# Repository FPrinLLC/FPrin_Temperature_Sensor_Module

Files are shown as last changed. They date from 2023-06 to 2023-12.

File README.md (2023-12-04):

# FPrin Temperature Sensor Module Development
Temperature measurement devices are ubiquitous in engineering and other scientific fields because temperature is a parameter that affects nearly all systems and is often essential to measure and control. Through recent work at FPrin involving temperature measurement and analysis we surveyed a series of temperature sensors and found that many common sensors have a surprisingly large rated accuracy specification. For example, perhaps the most used type of temperature measurement device, the thermocouple, typically has a range of ±1-2 °C. For some applications this is an acceptable level of accuracy, but often is insufficient. FPrin aims to develop a cost-effective, easy to build and program, highly accurate, and fully wireless temperature logging solution allowing for easily accessible, high confidence temperature measurement.

For FPrin's previously designed wired temperature sensor module, the design files can be found here:

[Wired Temperature Sensor Module Design](/z_Legacy-Designs/USB_Temperature_Sensor)

## Wireless Temperature Sensing Module
Step 2-2-2-5a

### Features:
- AS6221 Digital Temperature Sensor with rated accuracy of ±0.09 °C
- 3D Printed PLA Enclosure
- Assembly in under 1 hour
- Bluetooth Low Energy (BLE) Supported Data Logging
- High Capacity 2000 mAh Battery
- Companion MATLAB Application for visualization and Logging
- Programmable with Arduino IDE

### Datalogging Interface
To visualize and record data, we have written a MATLAB application that can easily connect with the temperature sensor module, and plot data at a desired frequency.



We've also saved a version of the app as an executable file, this way you won't need a license of MATLAB to use the application.

### Where to get started:
To get started with the temperature sensor module, check out the documentation:
- [User Manual](/FPR12104-00_2_RPT_Wireless_Temperature_Sensor_Module_User_Manual.pdf) : Guide for building, programming, and setting up the module
- [Bill of Materials](/FPR12096-00_1_BOM_Temperature_Sensor_Module.xlsx) : A full list of everything you'll need to build the module
- [MATLAB Application](/MATLAB-Application): A simple desktop app that allows you to connect to a temperature sensor module and log data
- [3D Print Files](/3D-Print-Files): STL and STEP Files for 3D printing the plastic housing
- [Microcontroller Source Code](/TemperatureSensor): Microcontroller source code used with Adafruit nRF52840 Dev Board

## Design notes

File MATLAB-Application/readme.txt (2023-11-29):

TemperatureSensorDatalogger Executable

1. Prerequisites for Deployment 

Verify that MATLAB Runtime(R2023b) is installed.   
If not, you can run the MATLAB Runtime installer.
To find its location, enter
  
    >>mcrinstaller
      
at the MATLAB prompt.
NOTE: You will need administrator rights to run the MATLAB Runtime installer. 

Alternatively, download and install the Windows version of the MATLAB Runtime for R2023b 
from the following link on the MathWorks website:

    https://www.mathworks.com/products/compiler/mcr/index.html
   
For more information about the MATLAB Runtime and the MATLAB Runtime installer, see 
"Distribute Applications" in the MATLAB Compiler documentation  
in the MathWorks Documentation Center.

2. Files to Deploy and Package

Files to Package for Standalone 
================================
-TemperatureSensorDatalogger.exe
-MCRInstaller.exe 
    Note: if end users are unable to download the MATLAB Runtime using the
    instructions in the previous section, include it when building your 
    component by clicking the "Runtime included in package" link in the
    Deployment Tool.
-This readme file 

3. Definitions

For information on deployment terminology, go to
https://www.mathworks.com/help and select MATLAB Compiler >
Getting Started > About Application Deployment >
Deployment Product Terms in the MathWorks Documentation
Center.

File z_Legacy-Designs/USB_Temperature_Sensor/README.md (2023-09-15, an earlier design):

# FPrin Temperature Sensor Module Development
Temperature measurement devices are ubiquitous in engineering and other scientific fields because temperature is a parameter that affects nearly all systems and is often essential to measure and control. Through recent work at FPrin involving temperature measurement and analysis we surveyed a series of temperature sensors and found that many common sensors have a surprisingly large rated accuracy specification. For example, perhaps the most used type of temperature measurement device, the thermocouple, typically has a range of ±1-2 °C. For some applications this is an acceptable level of accuracy, but often is insufficient. FPrin aims to provide a cost-effective, easy to build and program, and most importantly highly accurate temperature sensor module that allows the user to measure ambient temperature with a high degree of confidence.
## Temperature Sensing Module Rev. 1.0
Overview-ScrewBoss

### Features:
- AS6221 Digital Temperature Sensor with rated accuracy of ±0.09 °C
- 3D Printed PLA Enclosure
- Solder-free Assembly in under 1 hour
- Power and Data Transfer with USB Cable
- Programmable with Arduino IDE

### Housing configurations:
Overview-Both

The temperature sensor module has two different style of plastic housing, screw boss (left) and snap fit (right). The screw boss housing is assembled using 4 x thread-forming screws that securely fasten the upper and lower housing together. The snap fit housing uses a plastic flexure to secure the upper and lower housing together and can be removed without any tools.

### Where to get started:
To get started with the temperature sensor module, check out the User Manual and Bill of Materials! The User manual contains a step-by-step guide for building and programming a temperature sensor module in less than 1 hour. The Bill of Materials will tell you everything you need to build a temperature sensor module as well as links to where we bought our materials.

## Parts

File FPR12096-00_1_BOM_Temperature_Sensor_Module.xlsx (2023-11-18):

ASSY NO: |  |  |  | FPR12096
DESCRIPTION: |  |  |  | BLE Temperature Sensor Module
REV: |  |  |  | 1
PROJ # |  |  |  | FPR05
BOM Cost (USD): |  |  |  | $52.01
Item | Qty | UOM | P/N | Title | Vendor | Unit Cost | Total Cost | Link
1 | 0.167 | pack of 6 | B07LFD4LT6 | Solderless Breadboard | Amazon | $8.49 | $1.42 | https://www.amazon.com/gp/product/B07LFD4LT6/ref=ppx_yo_dt_b_asin_title_o02_s00?ie=UTF8&psc=1
2 | 1 | each | 4062 nRF52840 Feather | nRF52840 Feather | Adafruit | $24.95 | $24.95 | https://www.adafruit.com/product/4062
3 | 1 | each | 2011 3.7V Lipo Battery | 2000 mAh 3.7V Lipo Battery | Adafruit | $12.50 | $12.50 | https://www.adafruit.com/product/2011
4 | 1 | each | MIKROE-5466 | MikroE Thermoclick 28 | Mikroelektronika | $11.00 | $11.00 | https://www.mikroe.com/thermo-28-click
5 | 1 | each | FPR12097 | Bottom Housing | N/A | $0.00 | $0.00 | N/A
6 | 1 | each | FPR12098 | Upper Housing | N/A | $0.00 | $0.00 | N/A
7 | 0.08 | pack of 50 | 95495K18 | Rubber Feet | McMaster-Carr | $4.13 | $0.33 | https://www.mcmaster.com/95495k18/
8 | 2 | each | 5862K141 | Neodymium Magnets | McMaster-Carr | $0.77 | $1.54 | https://www.mcmaster.com/5862K141/
9 | 0.16 | pack of 25 | 99461A916 | M2 Threadforming Screws | McMaster-Carr | $8.62 | $1.38 | https://www.mcmaster.com/99461A916/

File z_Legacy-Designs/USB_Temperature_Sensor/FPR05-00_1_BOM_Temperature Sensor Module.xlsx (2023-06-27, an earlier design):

ASSY NO: |  |  | FPR12008
DESCRIPTION: |  |  | DIY Temperature Sensor Module
REV: |  |  | 1
PROJ # |  |  | FPR05
BOM Cost (USD): |  |  | $60.83
Item | Qty | P/N | Title | Vendor | Unit Cost | Link
1 | 1 | B07LFD4LT6 | Solderless Breadboard | Amazon | $7.59 | https://www.amazon.com/gp/product/B07LFD4LT6/ref=ppx_yo_dt_b_asin_title_o02_s00?ie=UTF8&psc=1
2 | 1 | ABX00034 | Arduino Nano 33 BLE | Amazon | $26.40 | https://www.amazon.com/gp/product/B07WXKWNQF/ref=ppx_yo_dt_b_asin_title_o02_s00?ie=UTF8&psc=1
3 | 1 | MIKROE-5466 | MikroE Thermoclick 28 | Mikroelektronika | $11.00 | https://www.mikroe.com/thermo-28-click
4 | 1 | FPR12089 | Bottom Housing | N/A | $0.00 | N/A
5 | 1 | FPR12090 | Upper Housing | N/A | $0.00 | N/A
6 | 1 | 95495K18 | Rubber Feet | McMaster-Carr | $4.13 | https://www.mcmaster.com/95495k18/
7 | 2 | 5862K141 | Neodymium Magnets | McMaster-Carr | $0.77 | https://www.mcmaster.com/5862K141/
8 | 2 | 2.00KXBK-ND | 2k Through-hole Resistor | Digikey | $0.10 | https://www.digikey.com/en/products/detail/yageo/MFR-25FBF52-2K/13070
9 | 1 | 497-16176-2-ND | 3.3V Linear Voltage Regulator | Digikey | $0.54 | https://www.digikey.com/en/products/detail/stmicroelectronics/L78L33ACZTR/1038305
10 | 1 | 399-9882-2-ND | 0.33 μF Ceramic Capacitor | Digikey | $0.49 | https://www.digikey.com/en/products/detail/kemet/C322C334M5U5TA7301/3726083
11 | 1 | 399-9859-2-ND | 0.1 μF Ceramic Capacitor | Digikey | $0.32 | https://www.digikey.com/en/products/detail/kemet/C315C104M5U5TA7303/3726116
12 | 1 | 99461A916 | M2 Threadforming Screws | McMaster-Carr | $8.62 | https://www.mcmaster.com/99461A916/

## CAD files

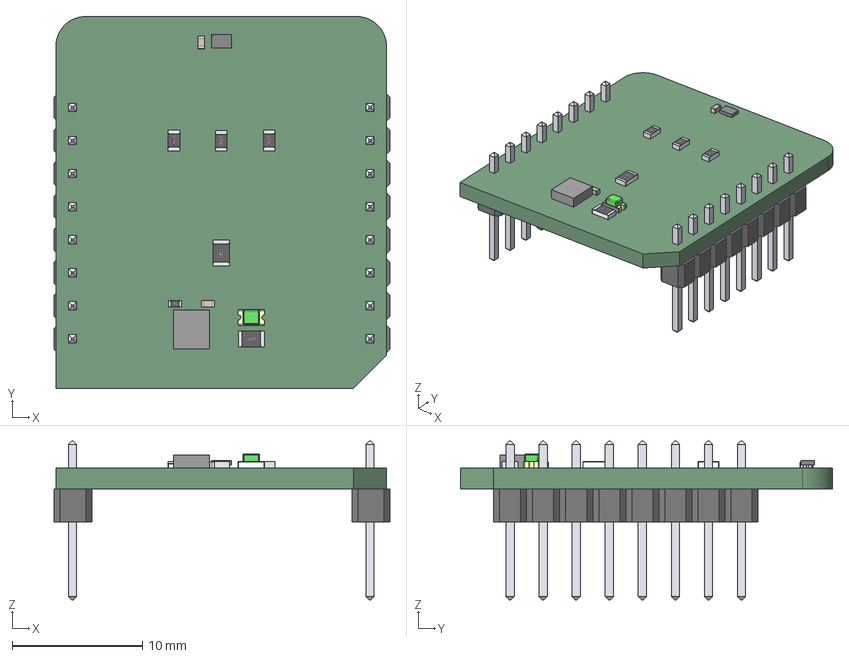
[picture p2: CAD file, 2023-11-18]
CAD/FPR12096/Thermo_28_click_v101.step
25.8 x 28.6 x 12.2 mm
Board
User_Library-R_0402
User_Library-R_0805 x 2
AS6221-AWLT-S_AMS
User_Library-R_0603 x 3
User_Library-SMD_CAPACITOR0402 x 2
User_Library-PinHeaderX5-1_PinHeaderX5_Body_1 x 4
User_Library-PinHeaderX5-1_PinHeaderX5_Pins_1 x 4
led_0805_green
Extruded

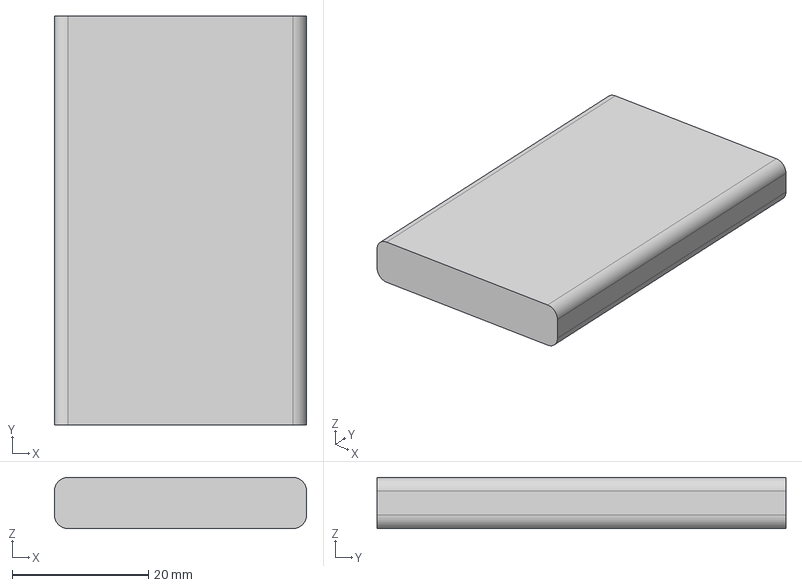
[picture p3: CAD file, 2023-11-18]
CAD/FPR12096/2011 2000mAh Battery.step
37.0 x 60.0 x 7.50 mm

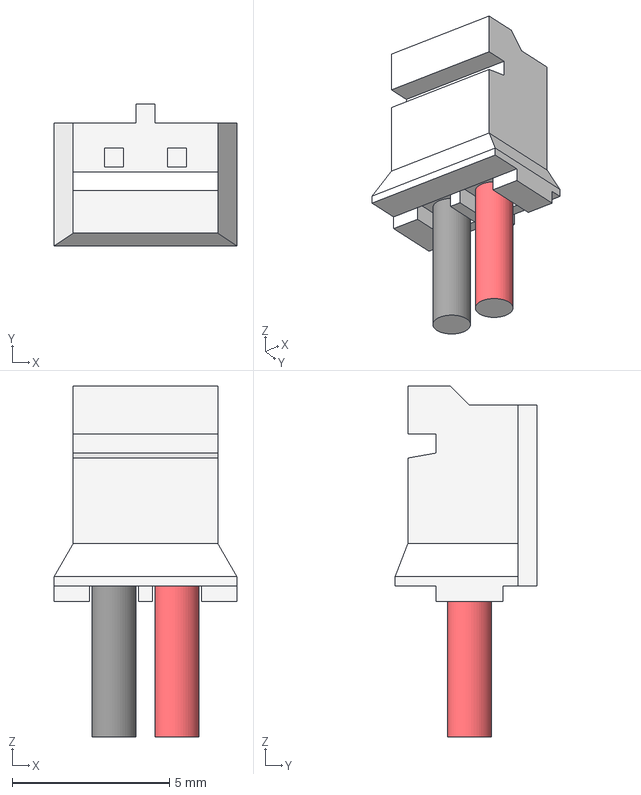
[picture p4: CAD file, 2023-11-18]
CAD/FPR12096/PHR-2-for-Battery-Adafruit.stp
5.80 x 4.50 x 11.2 mm

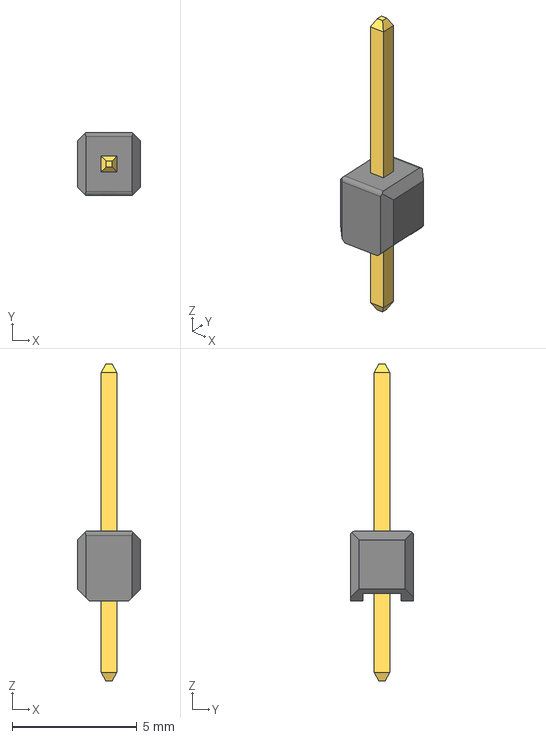
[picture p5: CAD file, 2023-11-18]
CAD/FPR12096/Pin Header 1x1 TH Pitch 2.54mm.stp
2.54 x 2.54 x 12.7 mm

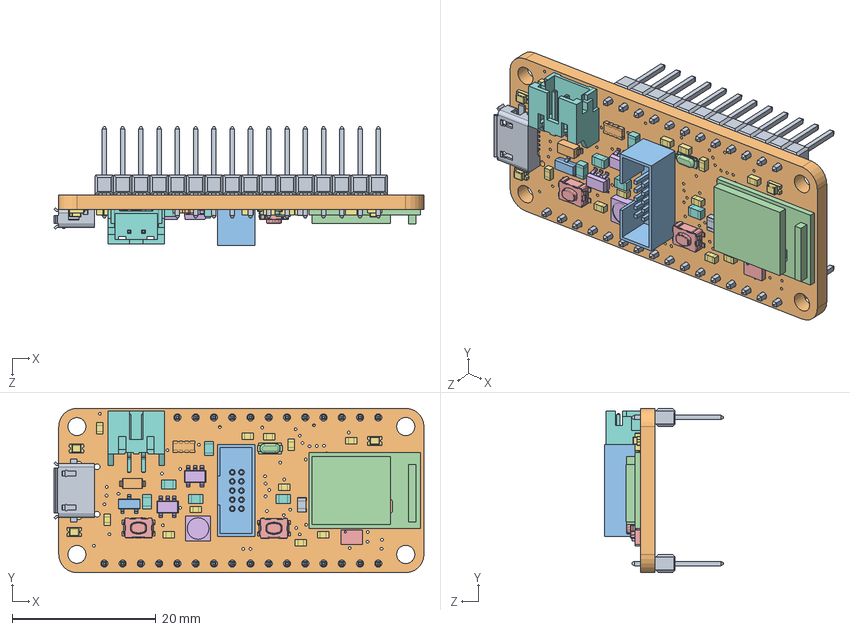
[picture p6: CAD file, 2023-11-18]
CAD/FPR12096/nRF52840 Feather.SLDASM
51.5 x 22.9 x 16.5 mm
Pin Header 1x1 TH Pitch 2.54mm^nRF52840 Feather x 28
Board^PCB Component_4062-nRF52830-Feather_nRF52840 Feather
2x5 0.05_^PCB Component_4062-nRF52830-Feather_nRF52840 Feather
32.768^PCB Component_4062-nRF52830-Feather_nRF52840 Feather
KMR2^PCB Component_4062-nRF52830-Feather_nRF52840 Feather x 2
AP2112(3.3V)^PCB Component_4062-nRF52830-Feather_nRF52840 Feather x 2
BLUE^PCB Component_4062-nRF52830-Feather_nRF52840 Feather x 3
JSTPH^PCB Component_4062-nRF52830-Feather_nRF52840 Feather
4u20329^PCB Component_4062-nRF52830-Feather_nRF52840 Feather
MBR120^PCB Component_4062-nRF52830-Feather_nRF52840 Feather
DMG2305^PCB Component_4062-nRF52830-Feather_nRF52840 Feather
MDBT50^PCB Component_4062-nRF52830-Feather_nRF52840 Feather
GD25Q16^PCB Component_4062-nRF52830-Feather_nRF52840 Feather
WS2812B3535^PCB Component_4062-nRF52830-Feather_nRF52840 Feather
0.1uF^PCB Component_4062-nRF52830-Feather_nRF52840 Feather x 11
10uF^PCB Component_4062-nRF52830-Feather_nRF52840 Feather x 5
DNP^PCB Component_4062-nRF52830-Feather_nRF52840 Feather
100K^PCB Component_4062-nRF52830-Feather_nRF52840 Feather

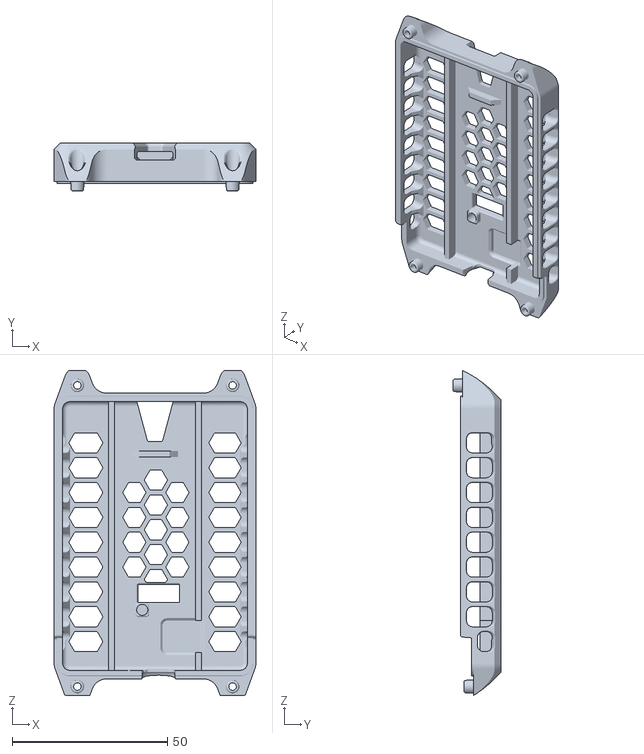
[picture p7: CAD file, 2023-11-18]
3D-Print-Files/FPR12098.STL
65.0 x 15.4 x 104.7

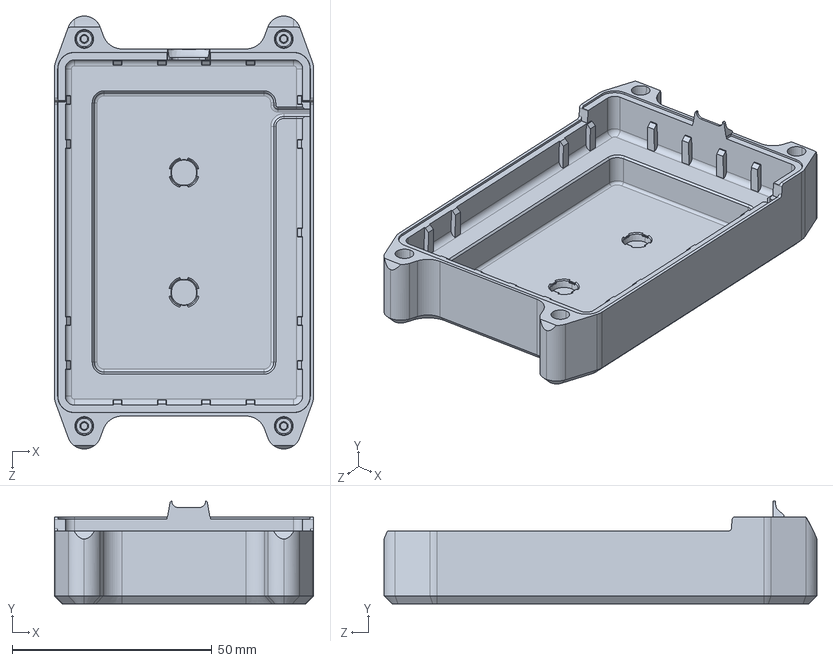
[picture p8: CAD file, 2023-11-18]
3D-Print-Files/FPR12097.STEP
65.0 x 25.8 x 108.5 mm

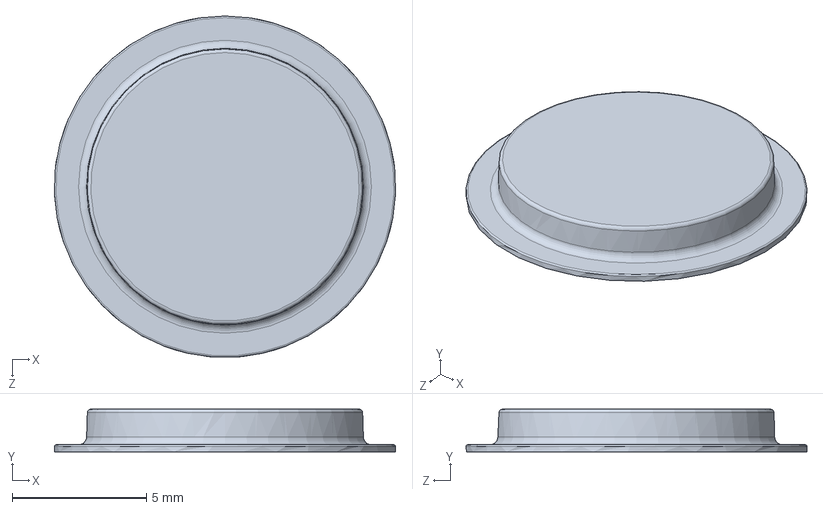
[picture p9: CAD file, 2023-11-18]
CAD/FPR12096/95495K18.SLDPRT
12.7 x 1.59 x 12.7 mm

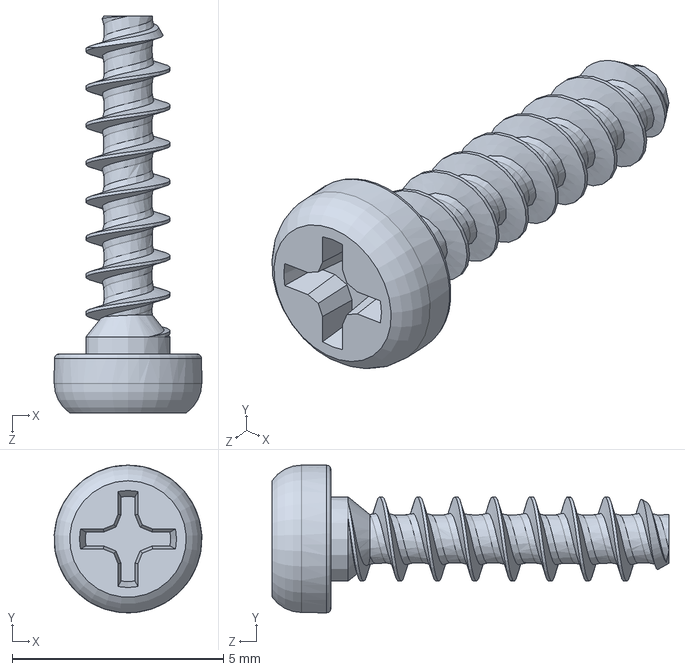
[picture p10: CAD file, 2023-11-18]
CAD/FPR12096/99461A916.SLDPRT
3.49 x 3.50 x 9.40 mm

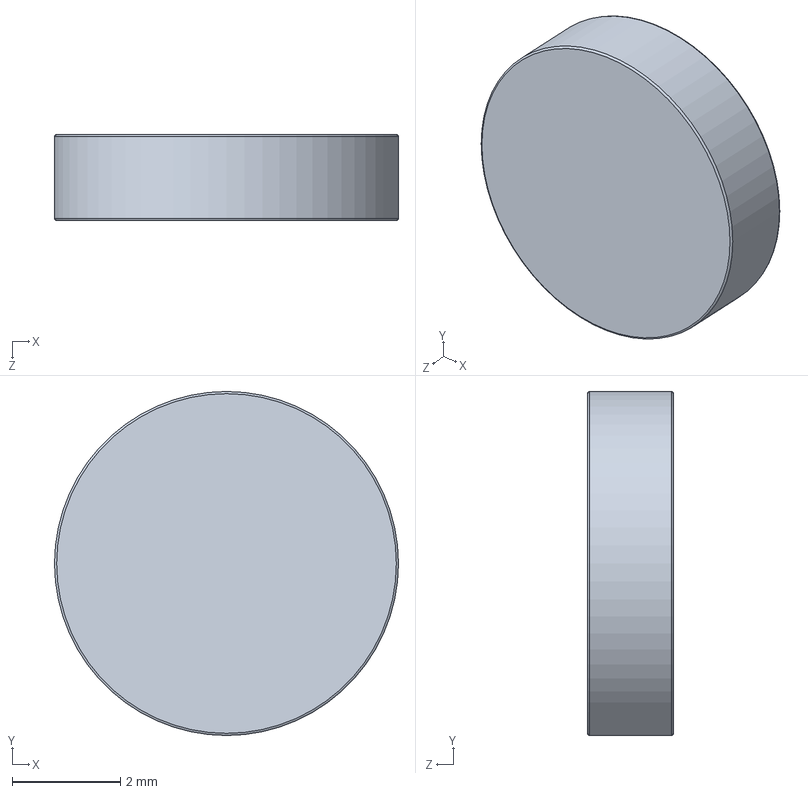
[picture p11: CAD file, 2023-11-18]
CAD/FPR12096/5862K141.SLDPRT
6.35 x 6.35 x 1.59 mm

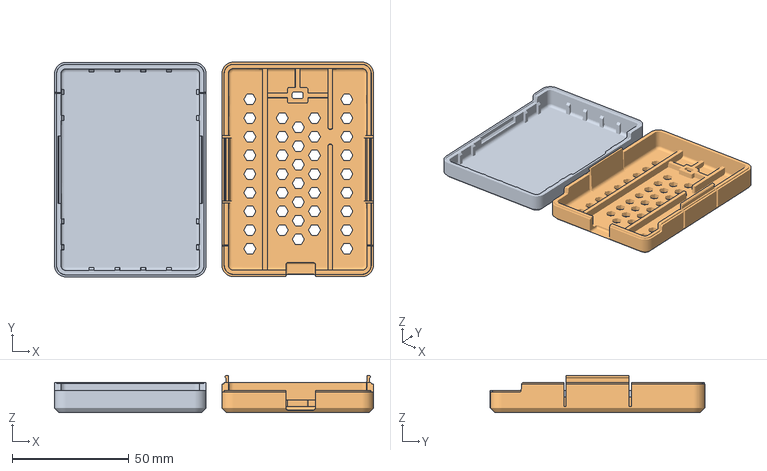
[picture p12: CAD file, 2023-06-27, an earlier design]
z_Legacy-Designs/USB_Temperature_Sensor/3D Print Files/Housing-SnapFit.3mf
136.8 x 92.1 x 16.1 mm
FPR12089-02.STL
FPR12090-02.STL

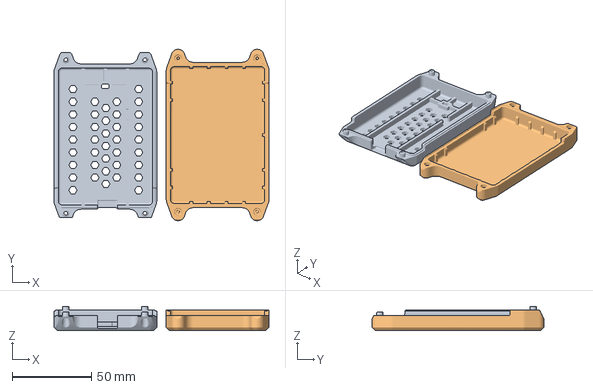
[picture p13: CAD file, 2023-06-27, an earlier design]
z_Legacy-Designs/USB_Temperature_Sensor/3D Print Files/Housing-ScrewBoss.3mf
136.0 x 108.5 x 15.4 mm
FPR12090-02-Screw.STL
FPR12089-02-Screw.STL

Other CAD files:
CAD/FPR12096/FPR12098.SLDPRT
3D-Print-Files/FPR12097.STL

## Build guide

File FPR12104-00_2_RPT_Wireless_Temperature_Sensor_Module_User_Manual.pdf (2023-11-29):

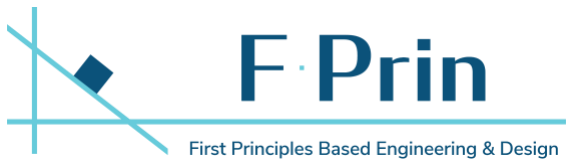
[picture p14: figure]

# BLE Temperature Sensor

# Module User Manual

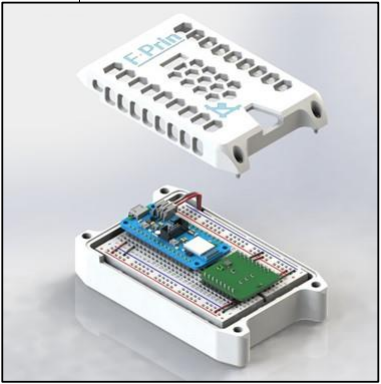
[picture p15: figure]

Document No. | FPR12095
Type | RPT
Revision | 01
State | In-Work
Authors | L Parrish
Project | FP05

BLE Temperature Sensor Module User Manual
Document No. FPR12104 | CONFIDENTIAL
Version: 00.1 | Page 2 of 22

## Contents

1 Introduction | 3
2 Assembly | 3
2.1 | Solderless Breadboard and Circuit | 3
2.1.1 | Materials and Tools | 3
2.1.2 | Solderless Breadboard Assembly Instructions | 5
2.2 | Module Housing | 8
2.2.1 | Materials and Tools | 8
2.2.2 | Module Housing Assembly Instructions | 10
3 Firmware Installation | 13
3.1 | Arduino IDE and nRF Board Manager Installation | 13
3.2 | Firmware Upload | 15
4 Datalogging Setup | 16
4.1 | Connecting to a Temperature Sensing Module | 16
4.2 | Plotting and Sample Frequency Tools | 17
4.3 | Datalogging Tools | 17
5 Revision History | 18
6 Appendix | 19
6.1 | Bill of Materials | 19
6.2 | Circuit Diagram | 20
6.3 | Plastic Part 3D Print Settings | 20

## 1 Introduction

Temperature measurement devices are ubiquitous in engineering and other scientific fields because temperature is a parameter that affects nearly all systems and is often essential to measure and control. Through recent work at FPrin involving temperature measurement and analysis we surveyed a series of temperature sensors and found that many common sensors have a surprisingly wide rated accuracy specification. For example, perhaps the most used type of temperature measurement device, the thermocouple, typically has a range of ±1-2 °C. For some applications this is an acceptable level of accuracy, but often is insufficient. FPrin aims to provide a cost-effective, easy to build and program, and most importantly highly accurate temperature sensor module that allows the user to measure ambient temperature with a high degree of confidence.

A primary development consideration was the accuracy of the temperature sensor used in the module. To achieve this, we incorporated the AS6221 digital temperature sensor from AMS. The integrated circuit features I²C communication for data transmission, low power consumption, and most importantly an excellent temperature accuracy rating of ±0.09 °C. Additionally, all components used to build the module can be easily sourced and assembled with minimal soldering and hand tools. Finally, a housing for the module can be easily fabricated using FDM 3D printing with PLA. The latest design features wireless data transfer to a host PC via Bluetooth Low Energy (BLE) communication and an easy-to-use interface for data visualization and logging. The CAD, Code, and documentation for the project are hosted on FPrin’s GitHub Repository Here:

https://github.com/FPrinLLC/FPrin_Temperature_Sensor_Module.git

## 2 Assembly

### 2.1 Solderless Breadboard and Circuit

### 2.1.1 Materials and Tools

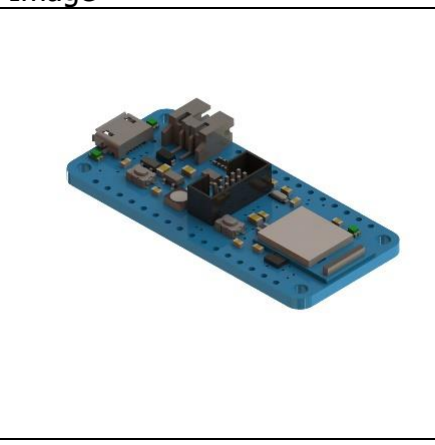
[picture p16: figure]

Description | Quantity | Image
nRF52840 Feather Development Board | 1

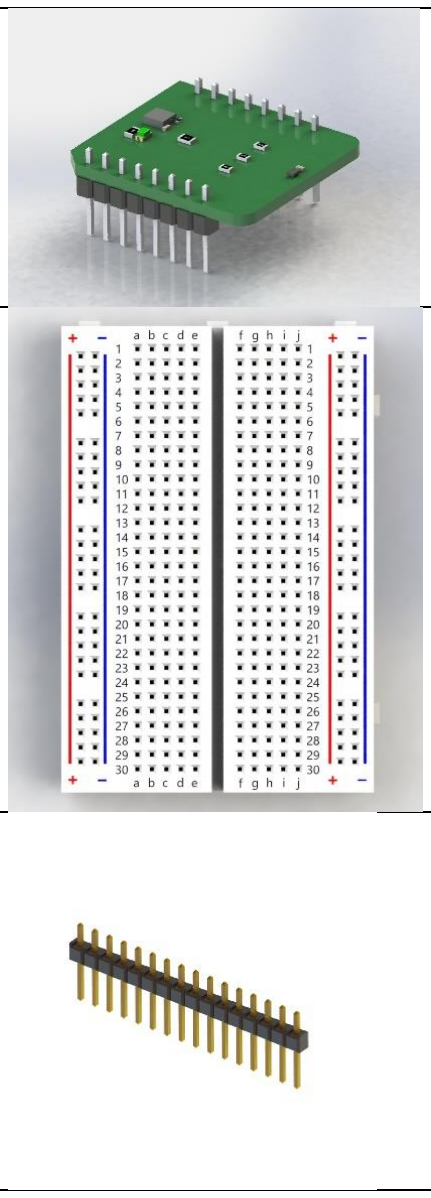
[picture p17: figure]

MikroE Thermo 28 Click PCBA | 1
Solderless Breadboard | 1
0.1” Pin Header Standoffs | 2 x 16
Breadboard Jumper Wires | ~6 inches

The following tools are required to assemble the solderless breadboard and circuit:

- Flush cutters
- Wire Strippers
- Soldering Iron
- Solder

### 2.1.2 Solderless Breadboard Assembly Instructions

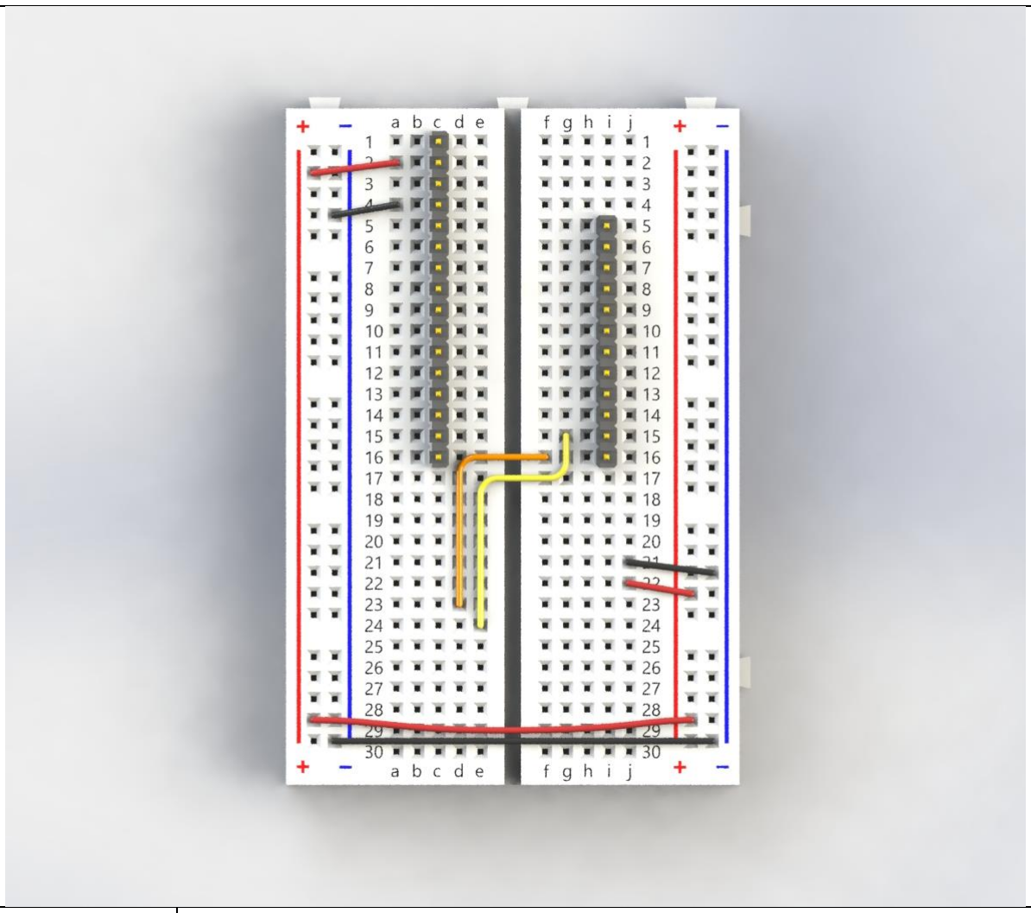
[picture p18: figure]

Step 1: | Install the pin headers into the solderless breadboard with the first row starting at position C1. Then cut the second pin header to remove 4 positions from the end, then install into position I5. Note that both rows should end at row 16.
Step 2: | Cut prototyping wire to length and insert into the breadboard as shown in the image above. Note that the wires should be pressed down flush to the top surface of the breadboard.

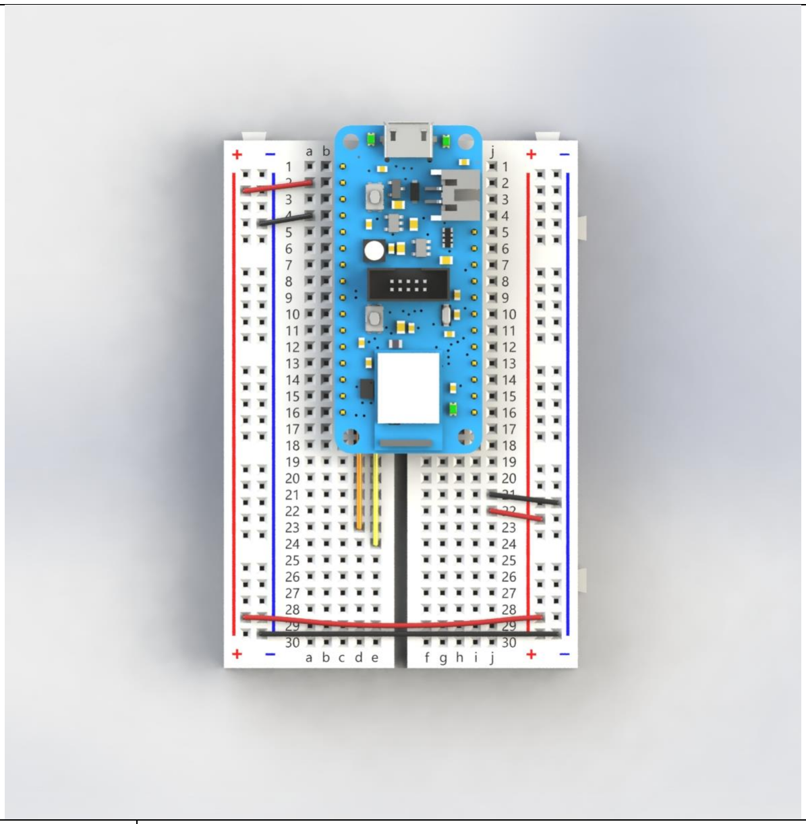
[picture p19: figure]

Step 3: | Place the nRF52840 Feather Dev. Board onto the pin headers as shown. Note that the upper left pin next to the USB connector is in breadboard position c1.
Step 4: | Solder the pin headers in place to secure the electrical connection using a soldering iron and solder.

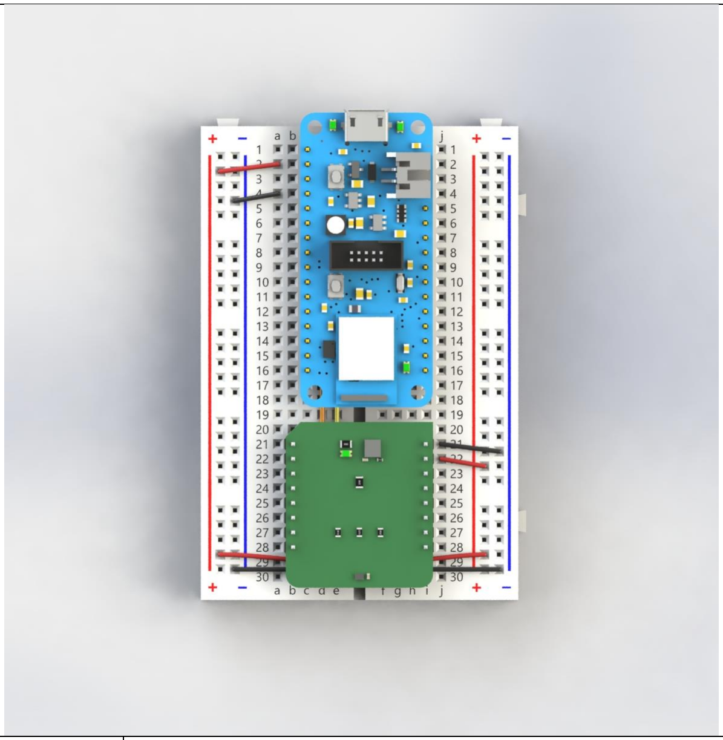
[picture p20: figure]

Step 5: | Press the MikroE Thermo 28 Click PCBA into the breadboard as shown. Note the pin labeled 3V3 should be in breadboard position I22.

### 2.2 Module Housing

### 2.2.1 Materials and Tools

The following parts are required to assemble the module housing:
Description | Quantity | Image
Solderless Breadboard Assembly | 1

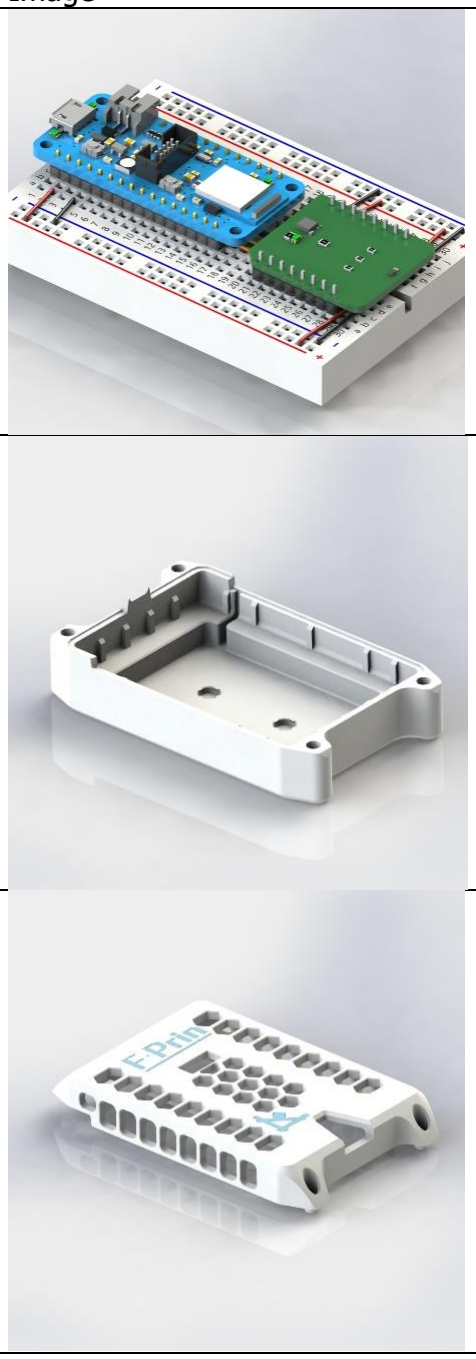
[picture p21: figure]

Housing Lower Half | 1
Housing Upper Half | 1

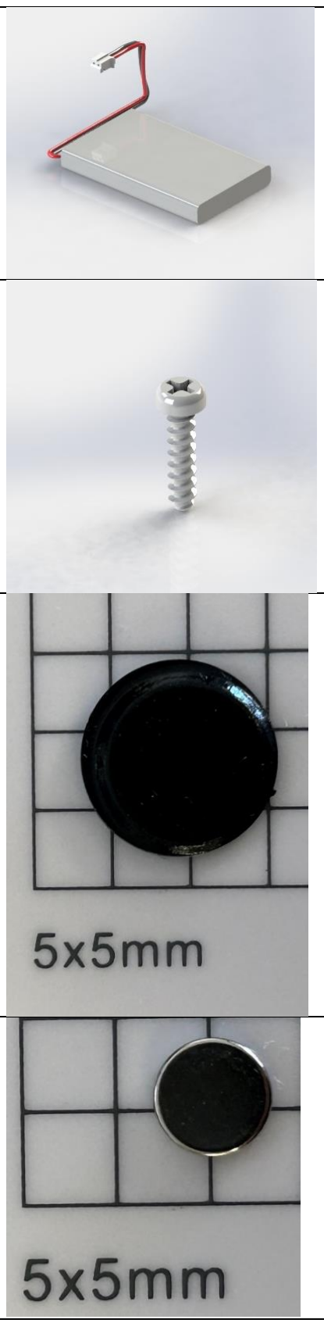
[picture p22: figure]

2000 mAh Li-Poly Battery | 1
Thread-forming Screws for Plastic | 4
Rubber Feet | 4
1/16” Thick, ¼” Neodymium Magnets* | 2

Assembly Tools:

- Size J0 Phillips Screw Driver

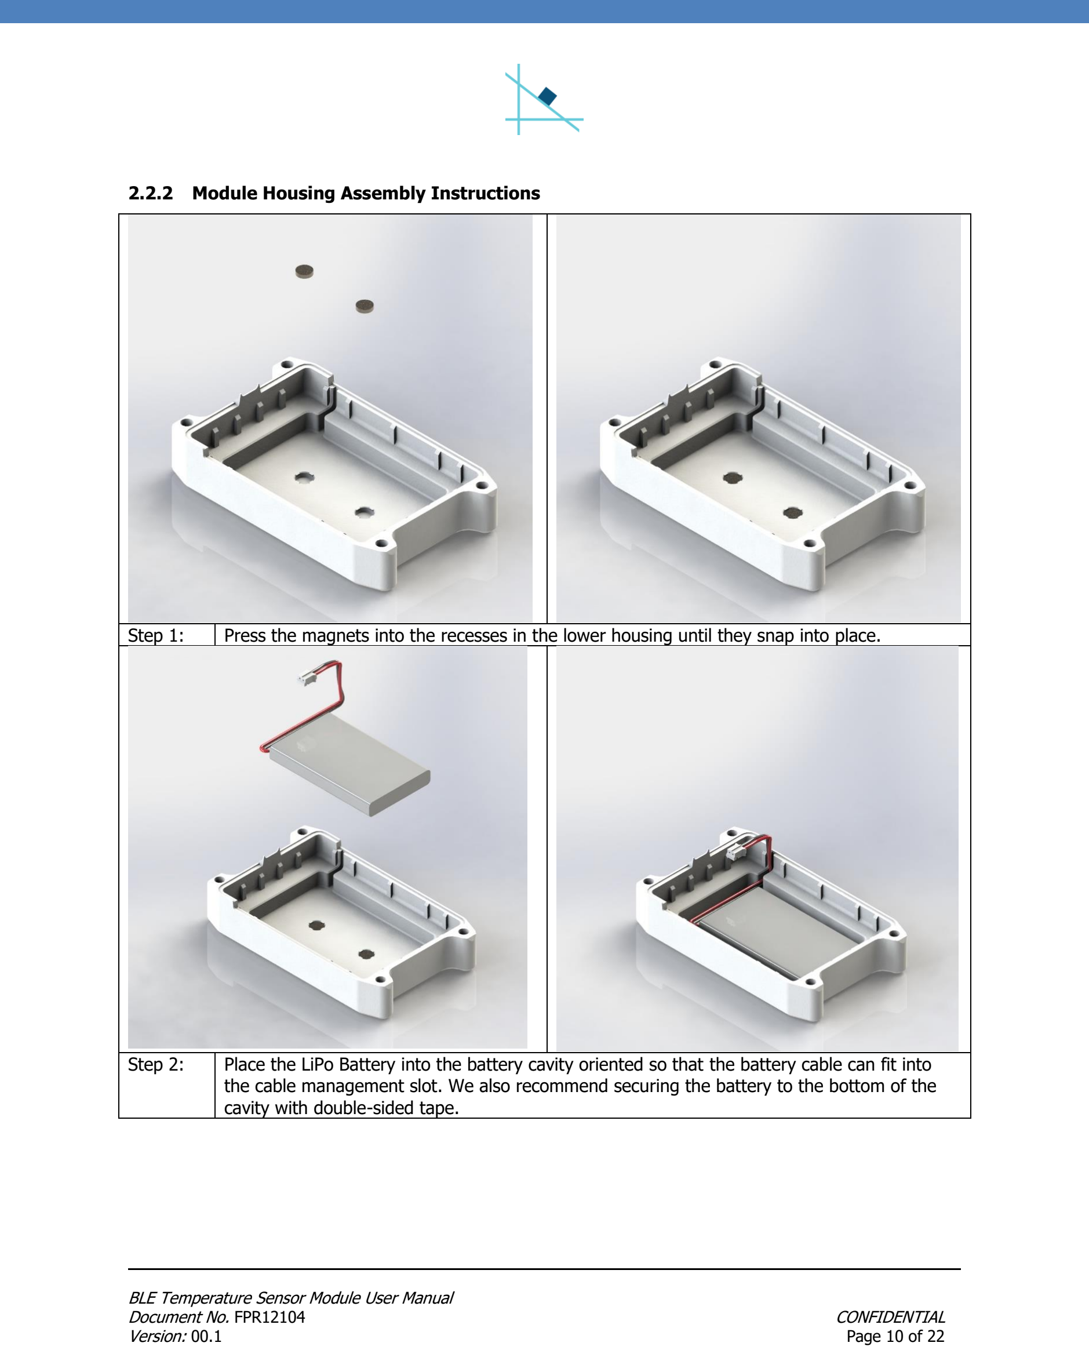
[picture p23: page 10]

### 2.2.2 Module Housing Assembly Instructions

Step 1: | Press the magnets into the recesses in the lower housing until they snap into place.
Step 2: | Place the LiPo Battery into the battery cavity oriented so that the battery cable can fit into the cable management slot. We also recommend securing the battery to the bottom of the cavity with double-sided tape.

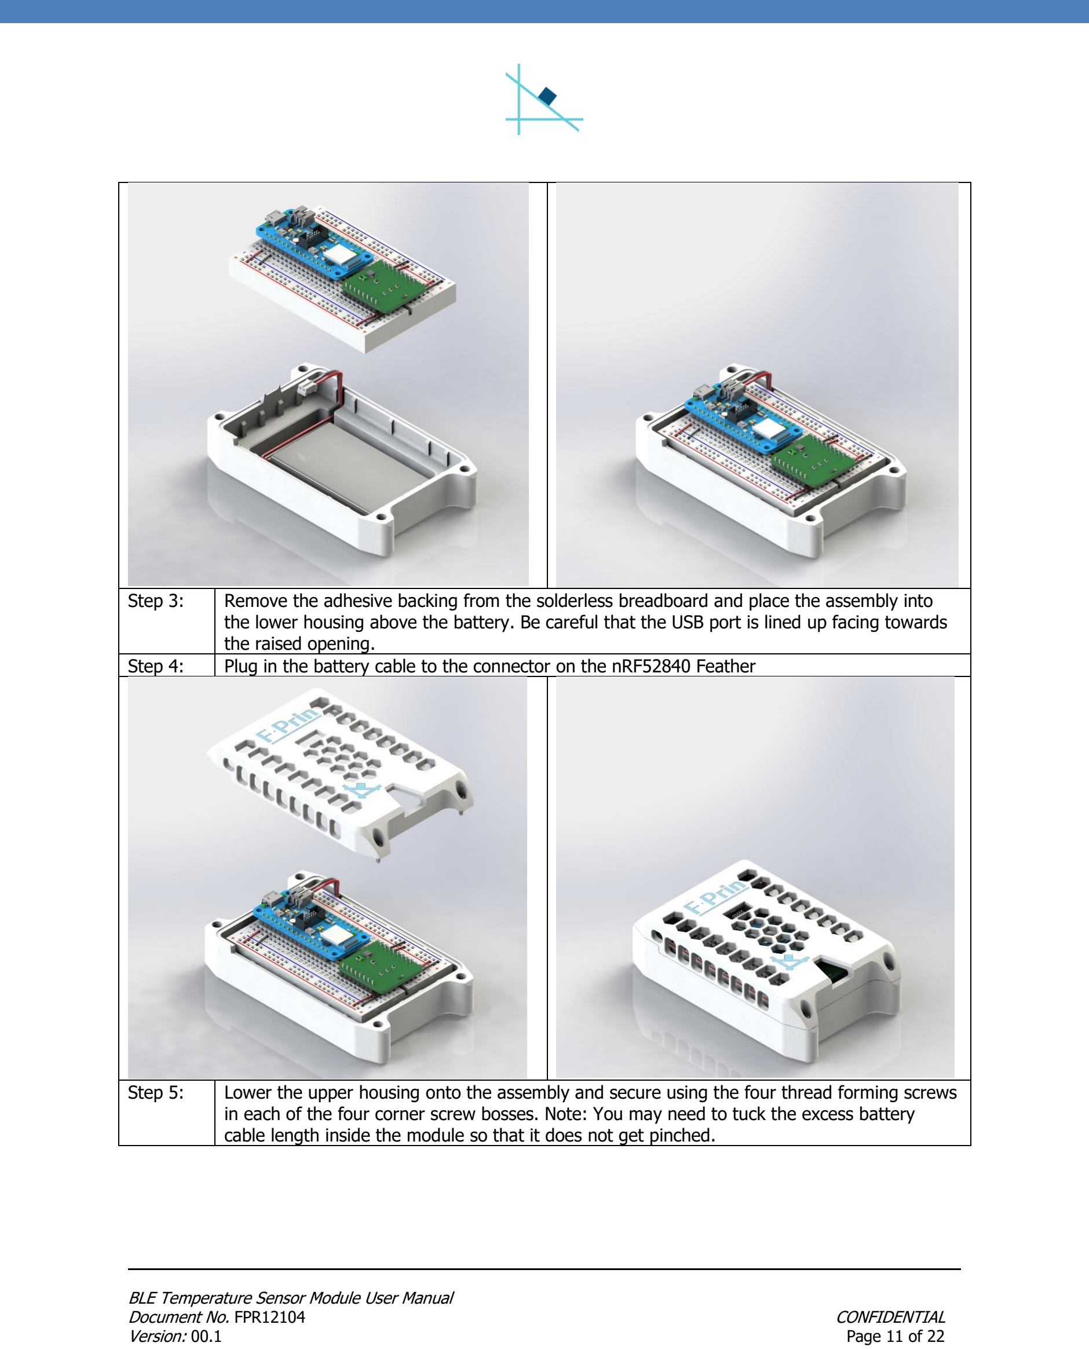
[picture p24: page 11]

Step 3: | Remove the adhesive backing from the solderless breadboard and place the assembly into the lower housing above the battery. Be careful that the USB port is lined up facing towards the raised opening.
Step 4: | Plug in the battery cable to the connector on the nRF52840 Feather
Step 5: | Lower the upper housing onto the assembly and secure using the four thread forming screws in each of the four corner screw bosses. Note: You may need to tuck the excess battery cable length inside the module so that it does not get pinched.

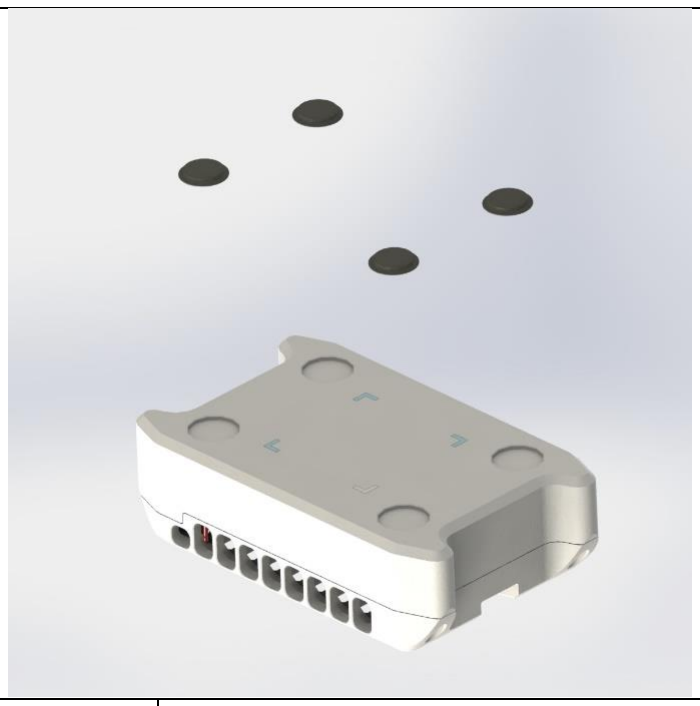
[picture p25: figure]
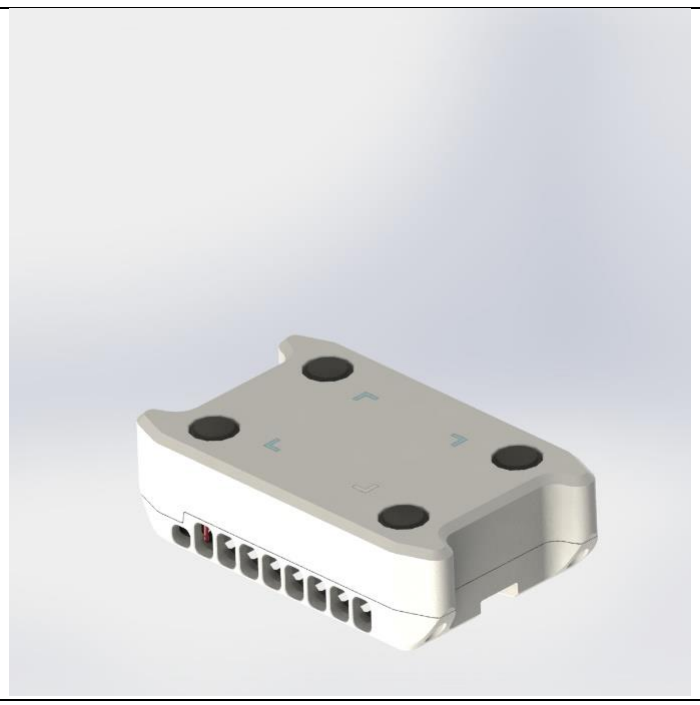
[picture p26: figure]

Step 8: Flip the module upside down, remove the adhesive backing on the rubber feet, then place into the large corner recesses to adhere.

## 3 Firmware Installation

### 3.1 Arduino IDE and nRF Board Manager Installation

To download the Arduino IDE required for programming, navigate to the following link and download the latest Arduino IDE version for your operating system: https://www.arduino.cc/en/software

After installing the Arduino IDE, launch the IDE and navigate to the Preferences Menu under File > Preferences. Under the “Additional Board Manager URLs” paste the following URL:

https://adafruit.github.io/arduino-board-index/package_adafruit_index.json

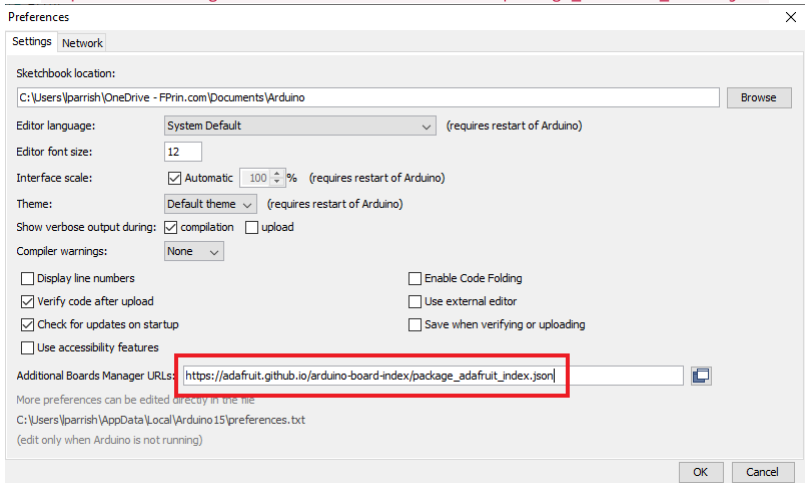
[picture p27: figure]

After adding the board manager URL, you will need to restart your Arduino IDE before continuing.

Next, navigate to the boards manager using the following path: Tools > Boards > Boards Manager

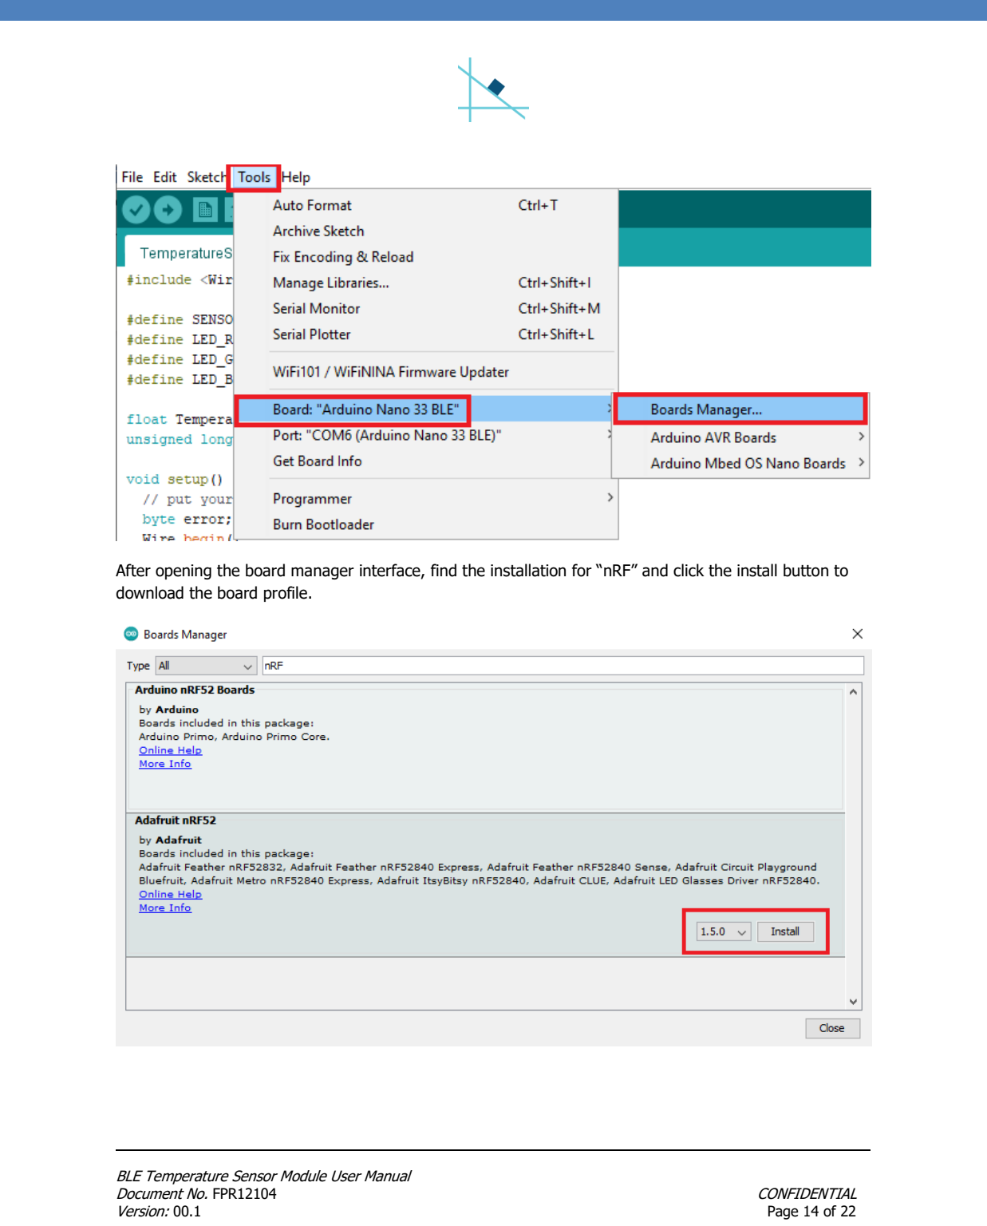
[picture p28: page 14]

After opening the board manager interface, find the installation for “nRF” and click the install button to download the board profile.

Finally, navigate to Tools > Boards > Adafruit nRF52 Boards > Adafruit Feather nRF52840

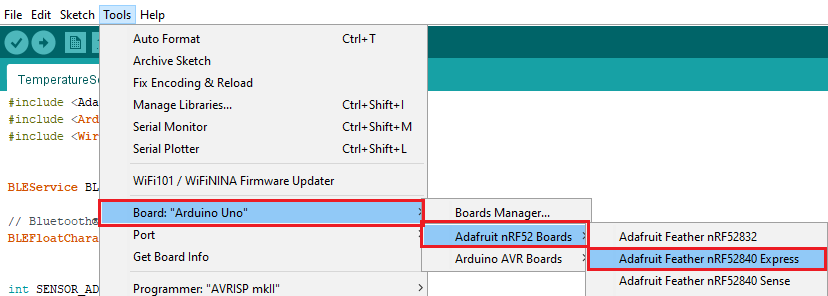
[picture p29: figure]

### 3.2 Firmware Upload

To upload the temperature sensor firmware to the nRF52840 Dev. Board, first connect the assembled temperature sensor module to the PC using a micro-USB cable. After first powering up, the LED’s on the microcontroller should light up indicating the board is receiving power. Then open the file “Temperature_Sensor.ino” in the Arduino IDE and select the COM port for the Dev. Board.

To download the source code, clone the Temperature sensor GitHub Repository from the link below:

https://github.com/FPrinLLC/FPrin_Temperature_Sensor_Module.git

To flash the firmware, click the Blue Arrow Icon at the top of the IDE. When the firmware is flashed, you will see the following message in the command log indicating that the firmware flash was successful.

After the firmware flash is complete, the temperature sensor module is ready to connect to a computer over Bluetooth, indicated by a blinking LED. See section 4 for more information on using the datalogging GUI.

## 4 Datalogging Setup

To log data wirelessly using the temperature sensor module, FPrin has developed a MATLAB application that can be used to connect to a temperature sensor via Bluetooth for Realtime data viewing and logging of data. The executable can also be found at FPrin’s Temperature Sensor GitHub repository. The basic interface is shown below:

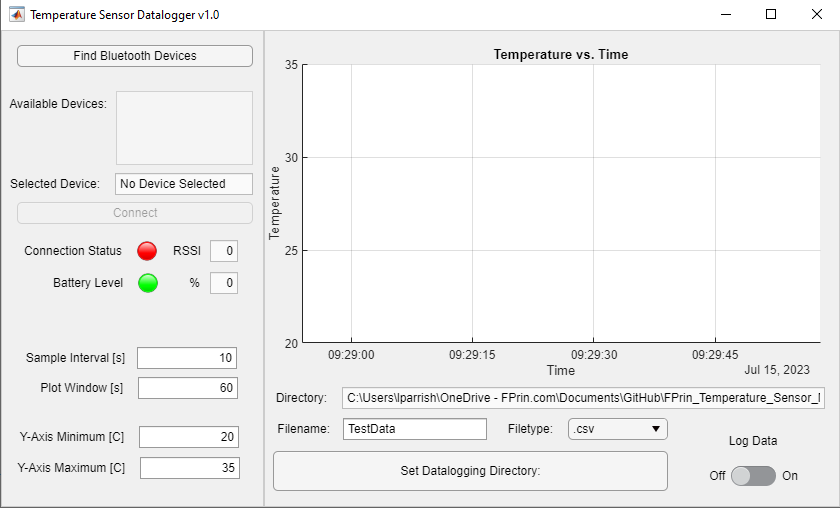
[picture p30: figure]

### 4.1 MATLAB Application Installation and Setup

An included standalone executable allows any system to run the datalogging application even without a MATLAB license. To install the application on a system without MATLAB:

1. First navigate the to Matlab Application folder from the root of the GitHub directory
2. If the MATLAB runtime has not been installed on your system, run the “RuntimeInstaller_web” executable. This will download the MATLAB runtime from MathWorks and install it.
3. After installing the runtime, you can launch the Datalogging application by running the “TemperatureSensorDatalogger” executable file. Note: It may be helpful to make a shortcut for the application executable to the Desktop for easy access.

### 4.2 Connecting to a Temperature Sensing Module

To begin using the datalogging and visualization interface, the first step is to find an available temperature sensor to connect to by clicking the “Find Bluetooth Devices” button which will populate the available devices menu below. Select the BLE device identifier to populate the selected device field, then click connect to initialize communication with the module.

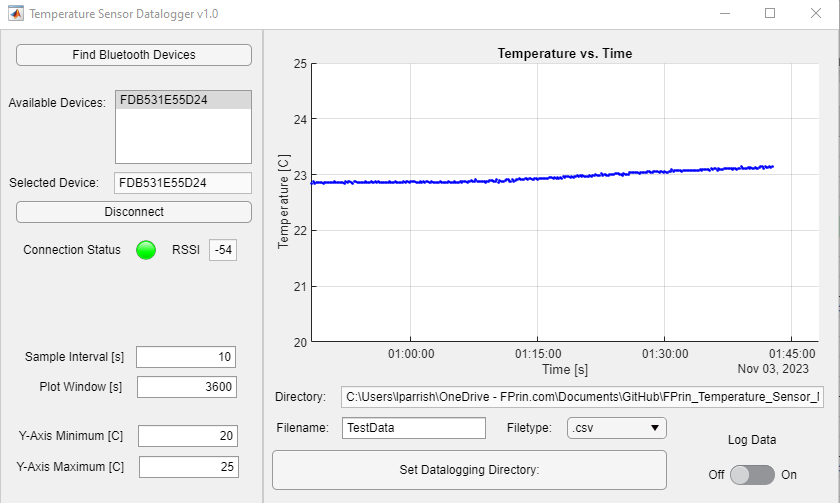
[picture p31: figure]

If a successful connection is made, the connection status lamp will turn green and display the RSSI signal strength and device battery level. Temperature data received from the device should also begin to update on the plot to the right. To disconnect from the temperature sensing module, click the disconnect button to stop receiving data.

### 4.3 Plotting and Sample Frequency Tools

To change the data sampling frequency, enter a new sampling frequency into the “Sample Interval” text field in seconds. To update the plot limits, the user can alter the horizontal axis scale in seconds, and the temperature axis minimum and maximum values in degrees Celsius.

### 4.4 Datalogging Tools

To capture data and save to a file, simply toggle the “Log Data” slide switch. When the switch is active, the interface will write the paired time and temperature data points to a datafile at the specified Sample Interval defined in the plot tools section. By default, datalogging files are saved as a CSV file format to your active MATLAB directory with a default filename of “TestData”. To change the default parameters, the “Set Datalogging Directory” button will allow the user to select the directory that all future datafiles will be saved to. Similarly, the test file name and filetype can be changed by using the text entry field and dropdown menu. Currently the interface supports saving files as CSV text files. Finally, each time the “Log Data” slide switch is turned on, the interface will create a new datalogging file with an appended auto-incrementing name to keep datafiles from separate log sessions independent. Note: the Datalogger will not be able to write to open CSV files.

## 5 Revision History

Rev | Description of Change | Project No. | Originator | Date
01 | Initial Draft | FP05 | L. Parrish | 29 Nov 2023

## 6 Appendix

### 6.1 Bill of Materials

ASSY NO: FPR12096

DESCRIPTION:

BLE Temperature Sensor
Module
REV: 1
PROJ # FPR05
BOM Cost (USD): $52.01
Qty | UOM | P/N | Title | Vendor

Unit
Cost

Total
Cost

0.167

pack
| of 6 | B07LFD4LT6 | Solderless Breadboard | Amazon | $8.49 | $1.42

1 each

| | 4062 nRF52840
| | Feather | nRF52840 Feather | Adafruit | $24.95 | $24.95
1 | each | 2011 3.7V Lipo
| | Battery | 2000 mAh 3.7V Lipo
| | | Battery | Adafruit | $12.50 | $12.50
1 each | MIKROE-5466 | MikroE Thermoclick 28 | Mikroelektronika | $11.00 | $11.00
1 | each | FPR12097 | Bottom Housing | N/A | $0.00 | $0.00
1 each | FPR12098 | Upper Housing | N/A | $0.00 | $0.00
0.08 | pack
| of 50 | 95495K18 | Rubber Feet | McMaster-Carr | $4.13 | $0.33
2 each | 5862K141 | Neodymium Magnets | McMaster-Carr | $0.77 | $1.54
0.16 | pack
| of 25 | 99461A916 | M2 Threadforming
| | | Screws | McMaster-Carr | $8.62 | $1.38

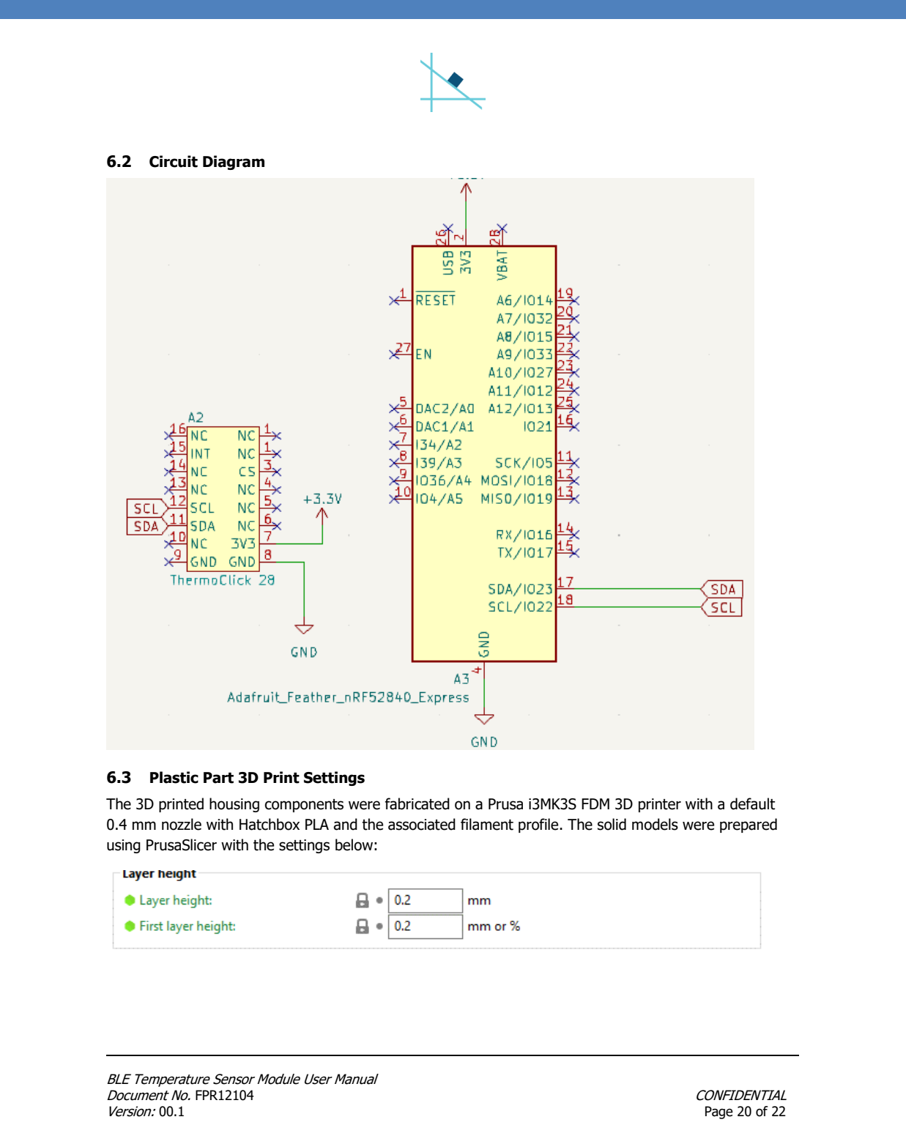
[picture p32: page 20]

### 6.2 Circuit Diagram

### 6.3 Plastic Part 3D Print Settings

The 3D printed housing components were fabricated on a Prusa i3MK3S FDM 3D printer with a default 0.4 mm nozzle with Hatchbox PLA and the associated filament profile. The solid models were prepared using PrusaSlicer with the settings below:

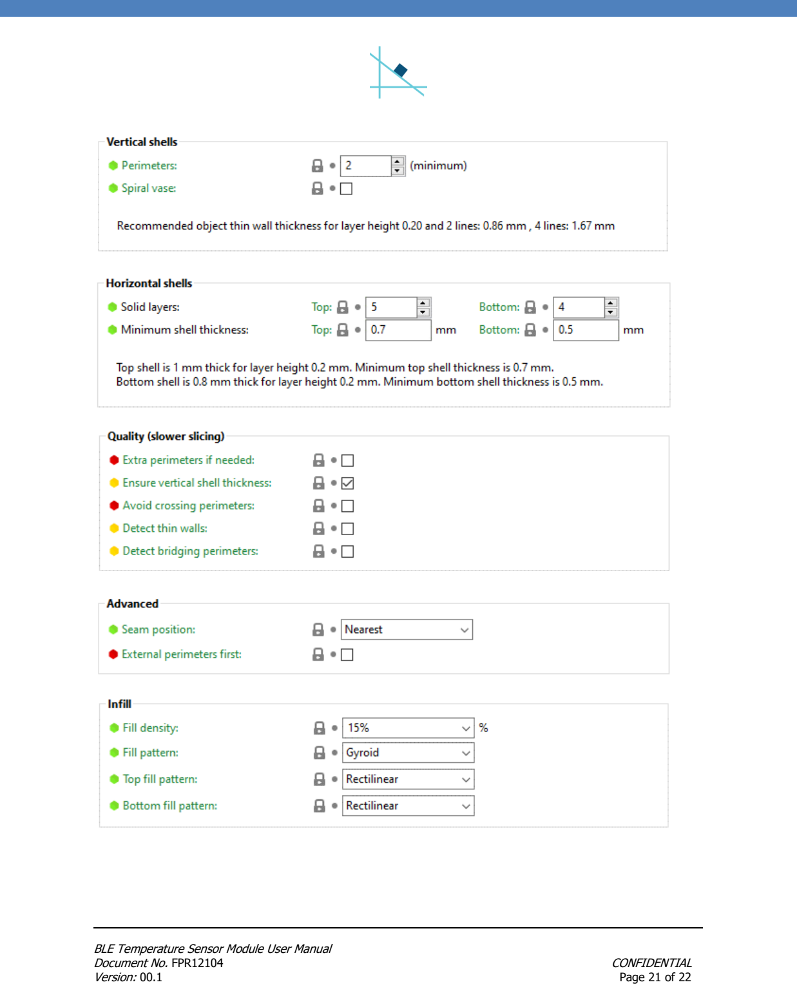
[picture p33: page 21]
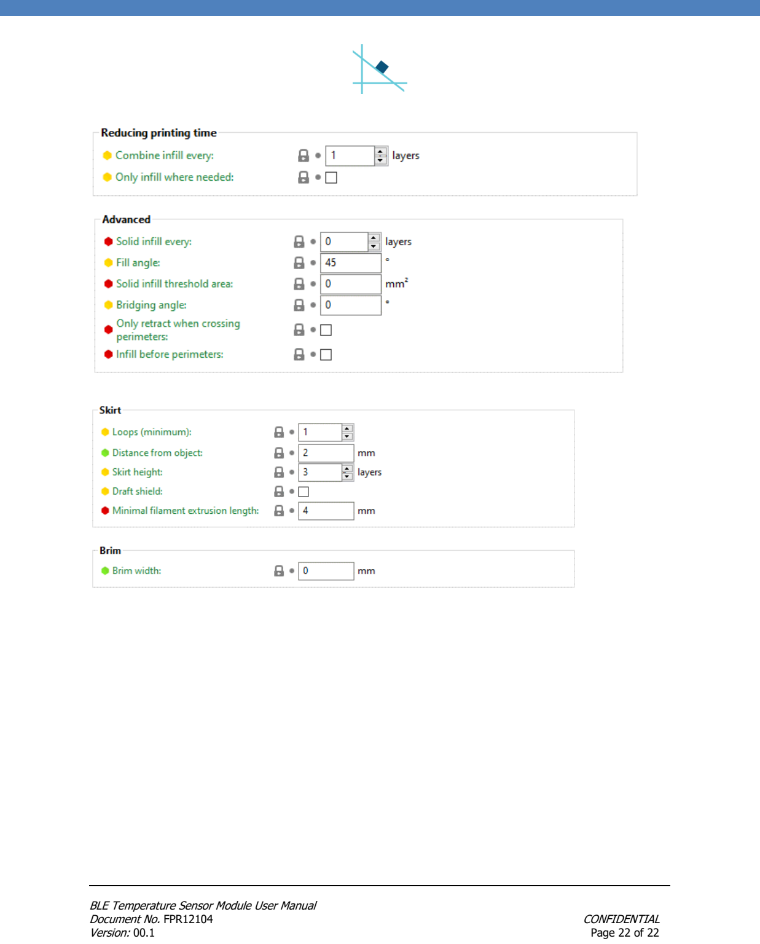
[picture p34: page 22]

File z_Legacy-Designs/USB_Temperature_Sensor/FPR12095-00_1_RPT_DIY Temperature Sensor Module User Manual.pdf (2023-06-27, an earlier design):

# DIY Temperature Sensor

# Module User Manual

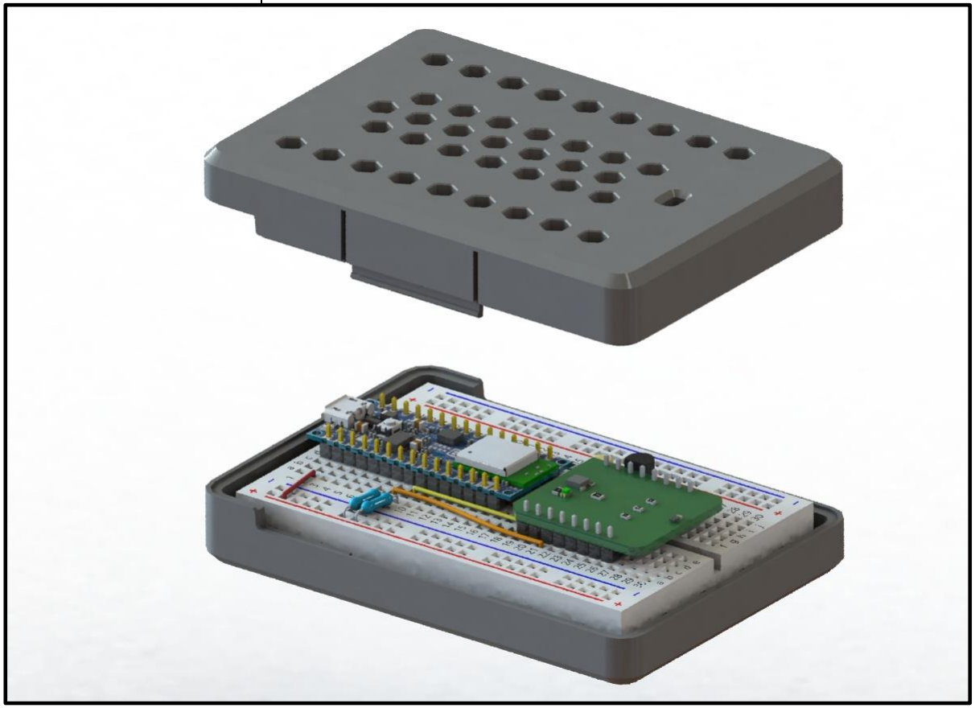
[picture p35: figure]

Document No. | FPR12095
Type | RPT
Revision | 01
State | In-Work
Authors | L Parrish
Project | FP05

DIY Temperature Sensor Module User Manual
Document No. FPR12095 | CONFIDENTIAL
Version: 00.1 | Page 2 of 23

## Contents

1 Introduction | 3
2 Assembly | 3
2.1 | Solderless Breadboard and Circuit | 3
2.1.1 | Materials and Tools | 3
2.1.2 | Solderless Breadboard Assembly Instructions | 5
2.2 | Module Housing | 11
2.2.1 | Materials and Tools | 11
2.2.2 | Module Housing Assembly Instructions | 13
3 Firmware Installation | 14
3.1 | Arduino IDE and Nano 33 BLE Board Manager Installation | 14
3.2 | Firmware Upload | 16
4 Datalogging Setup | 17
4.1 | Using the Arduino IDE Serial Terminal | 17
4.2 | Using Tera Term Serial Terminal | 18
5 Revision History | 19
6 Appendix | 20
6.1 | Bill of Materials | 20
6.2 | Circuit Diagram | 21
6.3 | Plastic Part 3D Print Settings | 21

## 1 Introduction

Temperature measurement devices are ubiquitous in engineering and other scientific fields because temperature is a parameter that affects nearly all systems and is often essential to measure and control. Through recent work at FPrin involving temperature measurement and analysis we surveyed a series of temperature sensors and found that many common sensors have a surprisingly large rated accuracy specification. For example, perhaps the most used type of temperature measurement device, the thermocouple, typically has a range of ±1-2 °C. For some applications this is an acceptable level of accuracy, but often is insufficient. FPrin aims to provide a cost-effective, easy to build and program, and most importantly highly accurate temperature sensor module that allows the user to measure ambient temperature with a high degree of confidence.

A primary development consideration was the accuracy of the temperature sensor used in the module. To achieve this, we incorporated the AS6221 digital temperature sensor from AMS. The integrated circuit features I²C communication for data transmission, low power consumption, and most importantly an excellent temperature accuracy rating of ±0.09 °C. Additionally, all components used to build the module can be easily sourced and assembled with no soldering and minimal hand tools. Finally, a housing for the module can be easily fabricated using FDM 3D printing with PLA. Currently there are two configurations for the module housing, one that joins the upper and lower housing with a plastic snap-fit flexure, and a second configuration that uses thread-forming screws for a more secure connection. The CAD, Code, and documentation for the project are hosted on FPrin’s GitHub Repository Here:

https://github.com/FPrinLLC/FPrin_Temperature_Sensor_Module.git

## 2 Assembly

### 2.1 Solderless Breadboard and Circuit

### 2.1.1 Materials and Tools

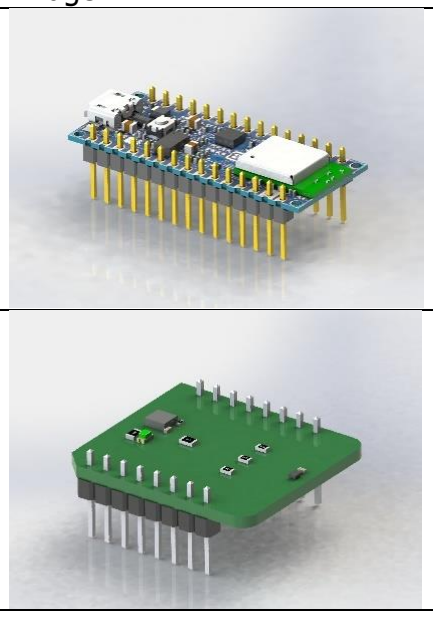
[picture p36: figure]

Description | Quantity | Image
Arduino Nano 33 BLE | 1
MikroE Thermo 28 Click PCBA | 1

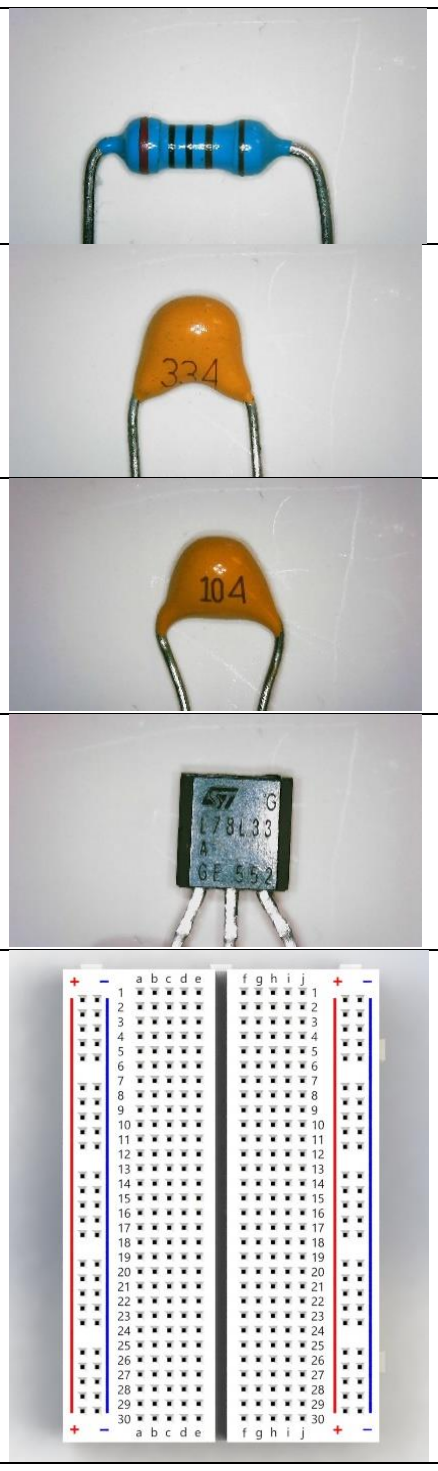
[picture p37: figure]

Through Hole Resistor 2 kΩ | 2
Through Hole Ceramic Capacitor 0.33 μF | 1
Through Hole Ceramic Capacitor 0.1 μF | 1
L878L33 Linear Voltage Regulator | 1
Solderless Breadboard | 1
Breadboard Jumper Wires | ~6 inches

The following tools are required to assemble the solderless breadboard and circuit:

- Flush cutters
- Wire Strippers

### 2.1.2 Solderless Breadboard Assembly Instructions

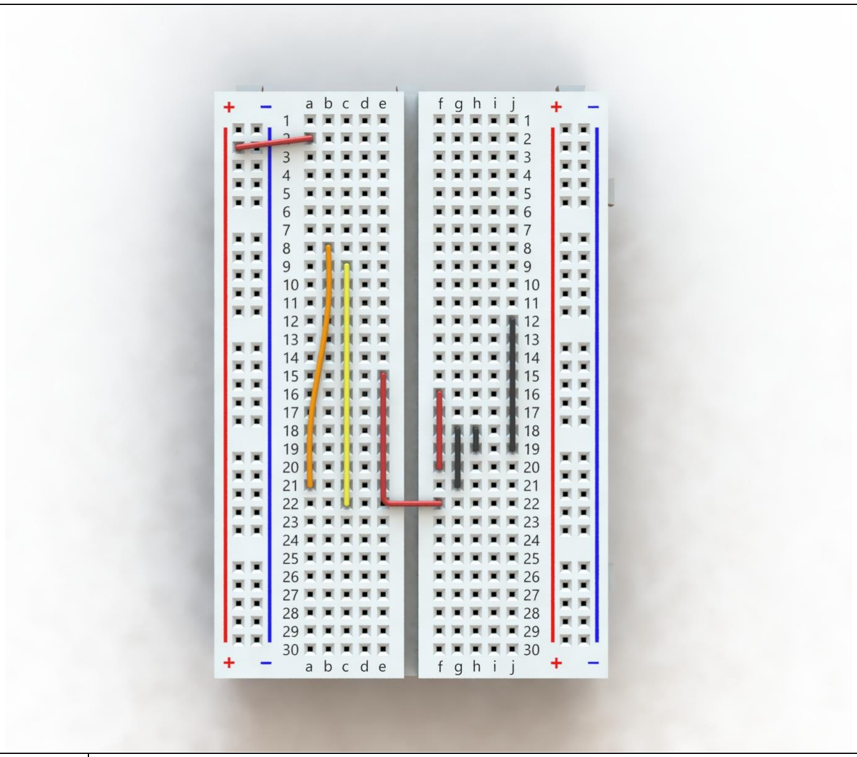
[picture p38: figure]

Step 1: Cut prototyping wire to length and insert into the breadboard as shown in the image above. Note that the wires should be pressed down flush to the top surface of the breadboard.

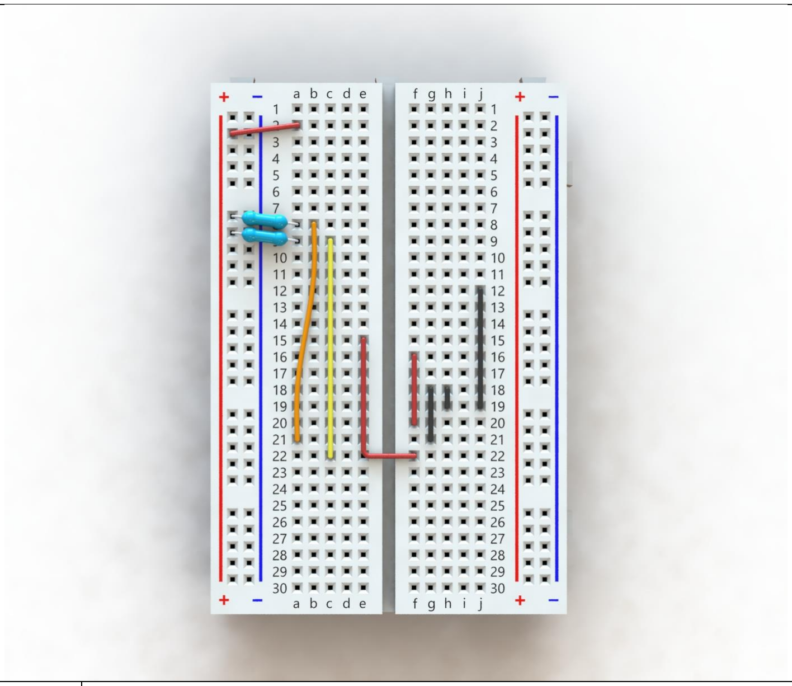
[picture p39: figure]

Step 2: | Connect the two 2k Resistors across the left positive voltage terminal and terminal rows 8 and 9.
Step 3: | Trim the leads of the L878L33 linear regulator to between 8-9 mm in length from the bottom of the IC. This will ensure the linear regulator is positioned close to the breadboard.

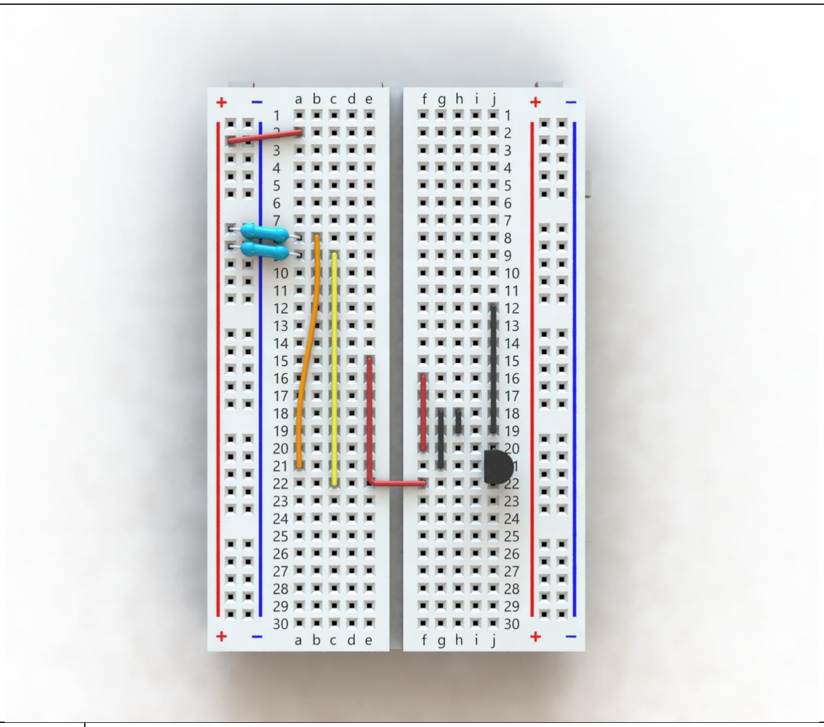
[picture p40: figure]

Step 4: Insert the linear regulator into the solderless breadboard as shown. Note that the flat side of the integrated circuit faces towards the center of the breadboard.

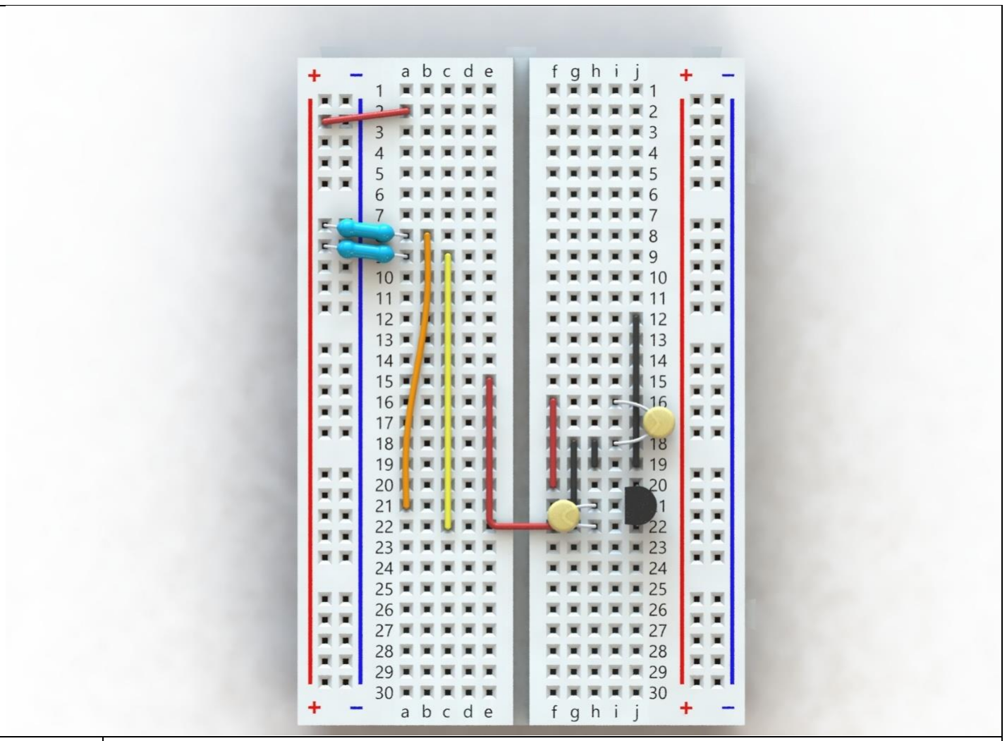
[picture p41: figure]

Step 5: Insert the ceramic capacitors into the solderless breadboard as shown. Note that the capacitor across rows 16 and 18 is the 0.1 μF capacitor and the capacitor across rows 21 and 22 is 0.33 μF. After inserting the capacitors into the breadboard, bend the capacitors down towards the surface of the breadboard as shown. This will ensure that the rest of the components can assemble without interference.

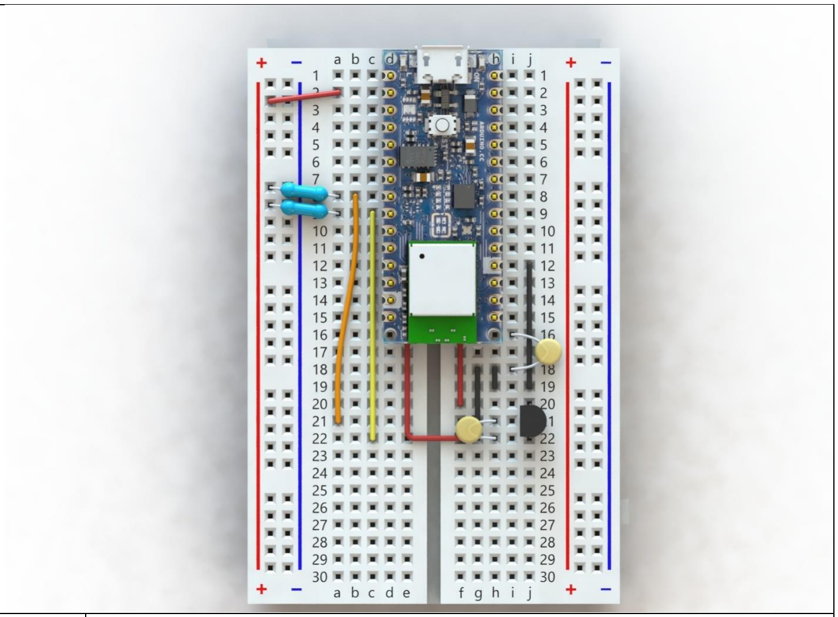
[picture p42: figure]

Step 6: Press the Arduino Nano 33 BLE into the breadboard as shown. Note that the upper left pin next to the USB connector is in breadboard position d1.

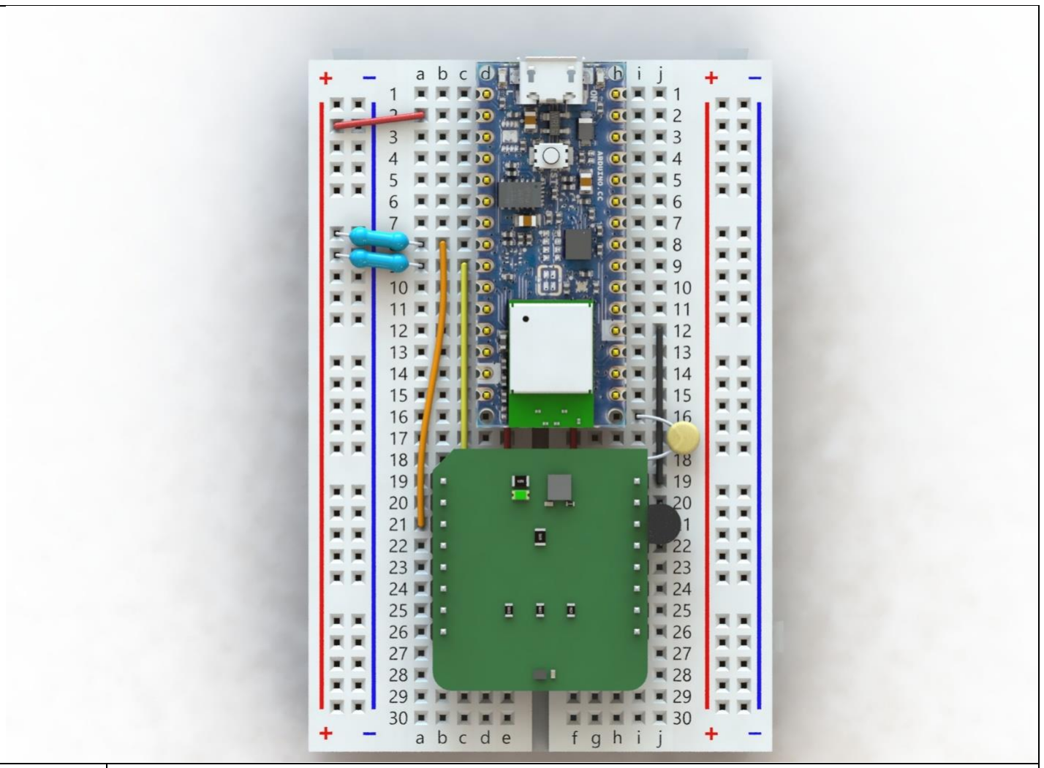
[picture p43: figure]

Step 7: Press the MikroE Thermo 28 Click PCBA into the breadboard as shown. Note the pin labeled 3V3 should be in breadboard position i20.

### 2.2 Module Housing

### 2.2.1 Materials and Tools

The following parts are required to assemble the module housing:
Description | Quantity | Image
Solderless Breadboard Assembly | 1

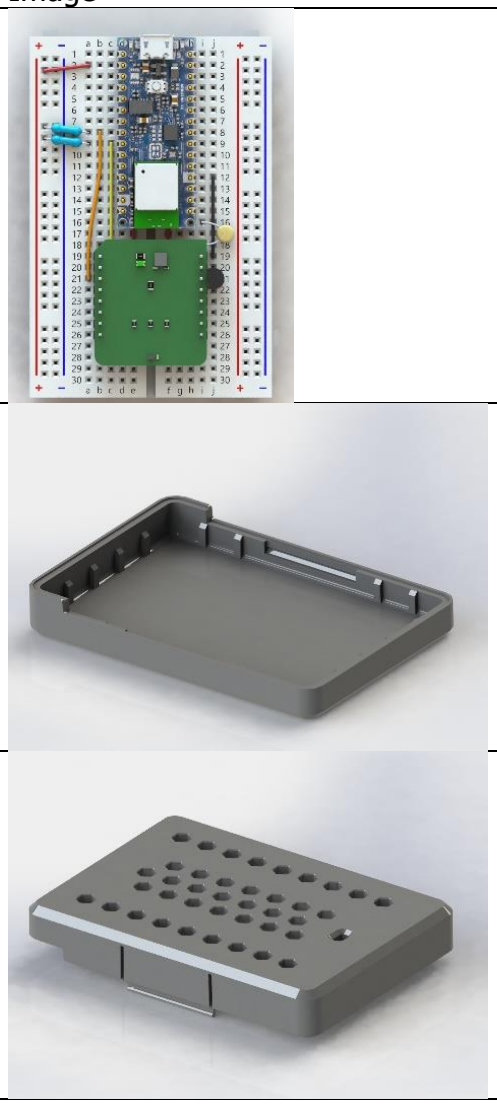
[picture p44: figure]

Housing Lower Half | 1
Housing Upper Half | 1

Rubber Feet | 4
1/16” Thick, ¼” Neodymium Magnets* | 2

*If adding magnets to the bottom of the module housing.

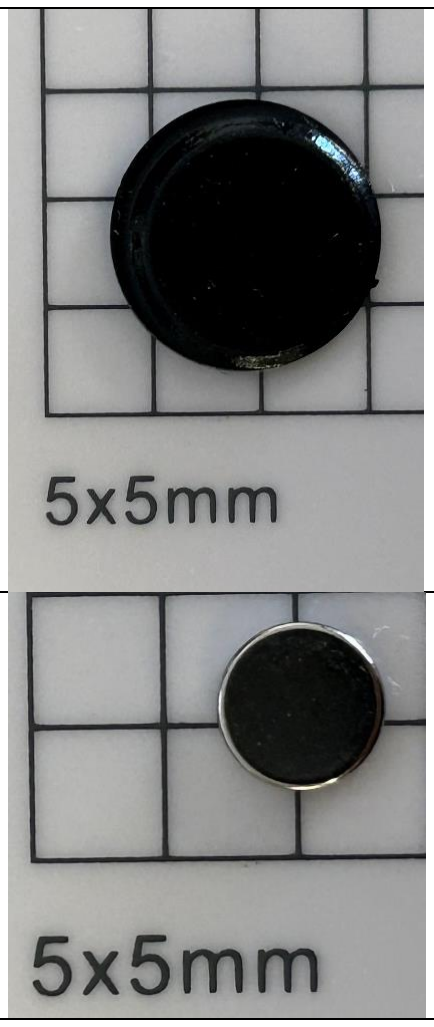
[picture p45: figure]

The following tools are required if adding magnets to the bottom of the module housing:

- Superglue or cyanoacrylate glue
- Gloves (nitrile or similar)

The following tools are required if building the housing configuration with screw bosses:

- Size J0 Phillips Screw Driver

### 2.2.2 Module Housing Assembly Instructions

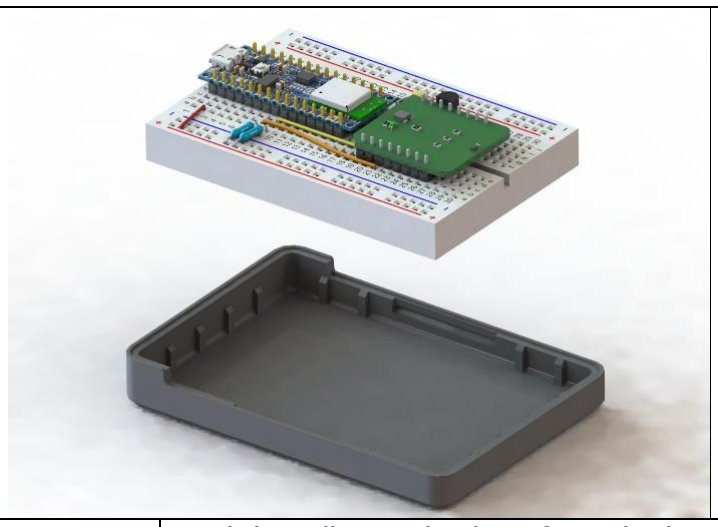
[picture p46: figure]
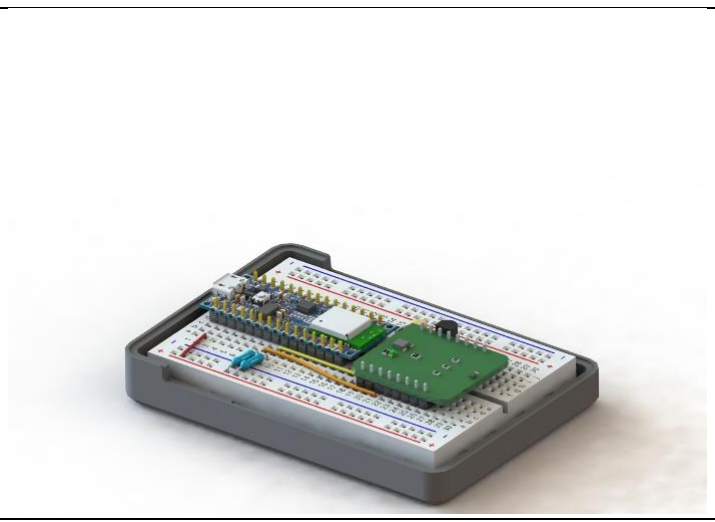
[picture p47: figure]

Step 1: | Peel the adhesive backing from the bottom of the solderless breadboard, then place the solderless breadboard in the lower housing so the USB connector is on the same side as the raised lip.
Step 2: | Press the breadboard down firmly to adhere the breadboard to the lower housing.

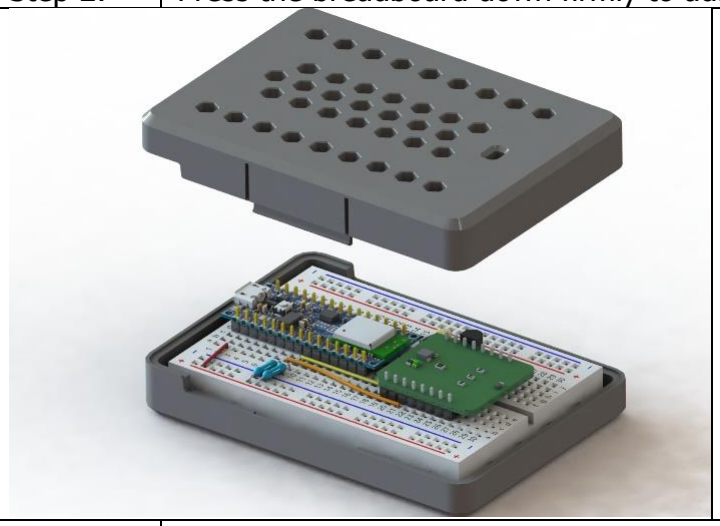
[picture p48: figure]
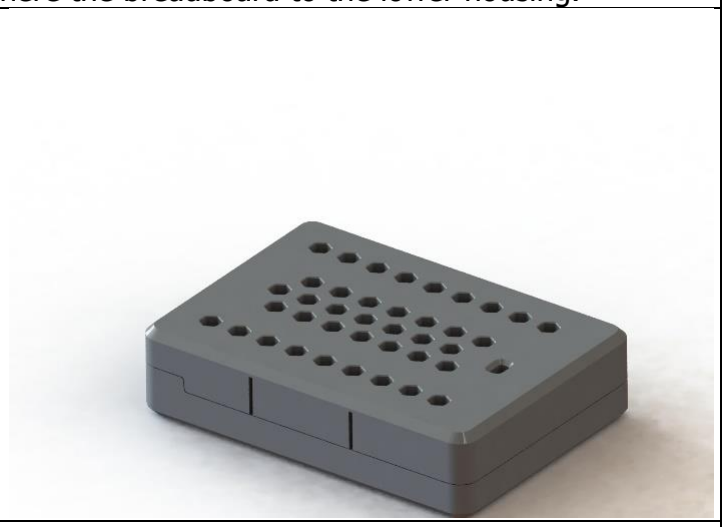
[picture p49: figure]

Step 3: | Align the upper housing with the lower housing, then press the upper housing down until the locking features click into place. Note: If building the housing configuration with screw bosses, insert the screws into the upper half of the enclosure, then tighten to secure using a Phillips screwdriver.

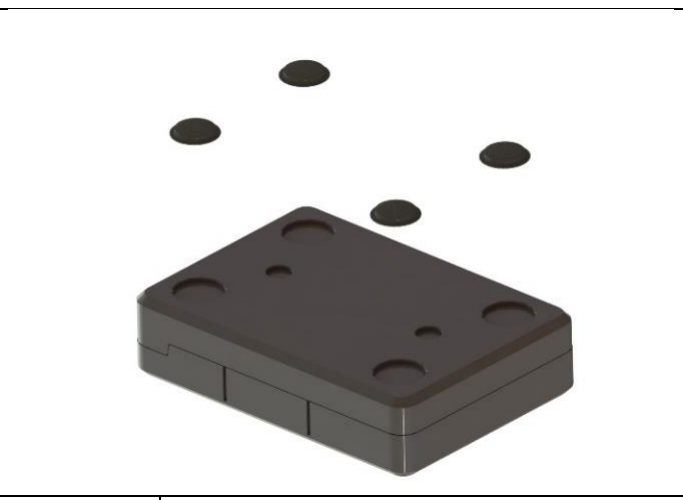
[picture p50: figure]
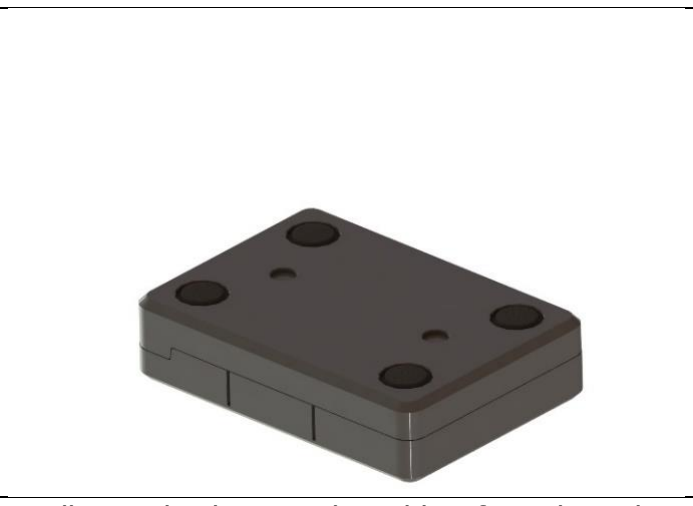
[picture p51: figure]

Step 4: | Flip the module upside down, remove the adhesive backing on the rubber feet, then place into the large corner recess to adhere.

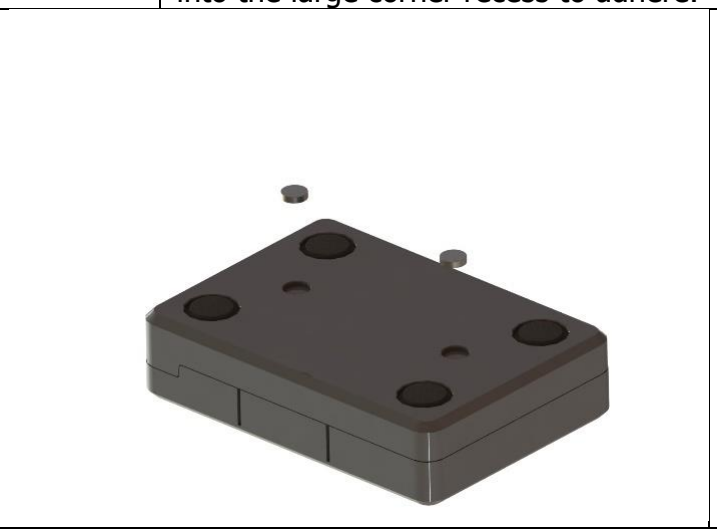
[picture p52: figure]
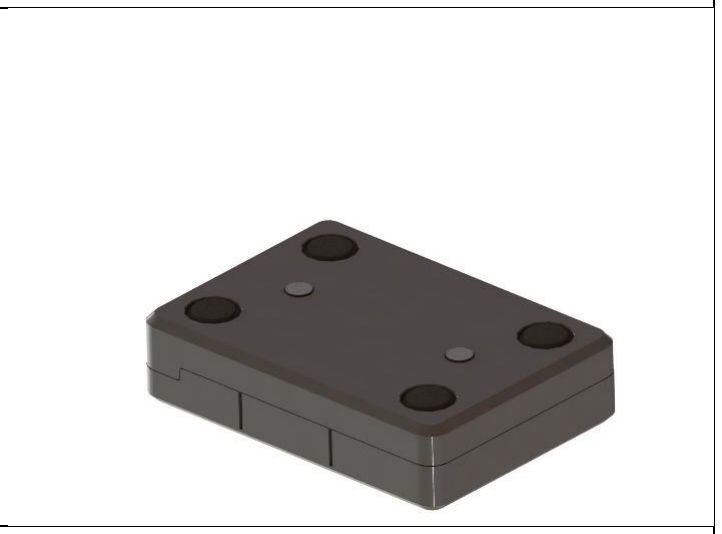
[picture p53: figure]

Step 5: | (Optional) Place a drop of glue in each of the smaller central recesses, then carefully press a magnet into each recess and wait at least 30 minutes for the glue to harden. During this process be sure to use gloves when handling super glue or cyanoacrylate glue.

## 3 Firmware Installation

### 3.1 Arduino IDE and Nano 33 BLE Board Manager Installation

To download the Arduino IDE required for programming, navigate to the following link and download the latest Arduino IDE version for your operating system: https://www.arduino.cc/en/software

After installing the Arduino IDE, launch the IDE and navigate to the boards manager using the following path: Tools > Boards > Boards Manager


After opening the board manager interface, find the installation for “Arduino Mbed OS Nano Boards” and click the install button to download the board profile.

Finally, navigate to Tools > Boards > Arduino Mbed OS Nano Boards > Arduino Nano 33 BLE

### 3.2 Firmware Upload

To upload the temperature sensor firmware to the Arduino, first connect the assembled temperature sensor module to the PC using a USB cable. Then open the file “Temperature_Sensor.ino” in the Arduino IDE and select the COM port for the Arduino Nano 33 BLE under the “Tools” tab. The Arduino sketch can be downloaded from the project GitHub Repository here:

https://github.com/FPrinLLC/FPrin_Temperature_Sensor_Module.git

To flash the firmware, click the Blue Arrow Icon at the top of the IDE. When the firmware is flashed, you will see the following message in the command log indicating that the firmware flash was successful.

## 4 Datalogging Setup

To test the temperature sensor the built-in serial monitor in the Arduino IDE can be used to easily access temperature data and test the module. For longer term temperature measurement and datalogging, we recommend Tera Term, an open-source terminal simulator that can log data to an output file with a timestamp.

To connect to the temperature sensor module, you’ll need to connect to your PC using a USB micro to USB Type A cable. After plugging in the module, the green LED on the MikroE PCBA should light up indicating that the PCBA is receiving power.

### 4.1 Using the Arduino IDE Serial Terminal

After connecting the module to power, open the Arduino IDE and select the COM port for the module using the same procedure in section 3.2. Then click the serial monitor icon in the top right corner of the Arduino IDE:

The serial monitor should open in a new window and request the user for a sampling interval. This is the time interval in seconds between temperature measurements reported by the temperature sensor module.

To enter the sampling interval, type a numeric value into the entry bar at the top of the serial monitor, then, click the send button or press enter.

After the command is sent, the serial monitor will confirm the sampling interval and begin printing temperature data to the serial monitor.

### 4.2 Using Tera Term Serial Terminal

To download Tera Term, use the following link: https://ttssh2.osdn.jp/index.html.en

After connecting the module to power through the USB cable, launch Tera Term and select ‘Serial’ for a new connection type followed by the COM port, then press ‘OK’ to connect.


After connecting to the temperature sensor module, a terminal window will pop-up and request a sampling interval in seconds. Enter the sampling interval in seconds and the module will begin acquiring data.

To log data to a file, navigate to File > Log and a pop-up will request a location to save the file as well as a file name. Additionally, there are several check box options for the saved data file, which we
recommend selecting Timestamp, Append, and Plain Text.

Click Save when ready to begin logging data. Now as long as the terminal is open, any data received will be appended to the datafile that can easily be read using a text editor such as notepad or imported into a spreadsheet or data analysis tool like MS Excel.

To stop logging data, navigate to File > Stop Logging. To disconnect from the temperature sensor module, navigate to File > Exit, this will close the terminal and stop receiving data.

## 5 Revision History

Rev | Description of Change | Project No. | Originator | Date
01 | Initial Draft | FP05 | L. Parrish | 20 Jun 2023

## 6 Appendix

### 6.1 Bill of Materials

ASSY NO: FPR12008
DESCRIPTION: DIY Temperature Sensor Module
REV: 1
PROJ # FPR05
BOM Cost (USD): $52.21
Item Qty P/N | Title | Vendor | Unit Cost
1 | 1 B07LFD4LT6 | Solderless Breadboard | Amazon | $7.59
2 | 1 ABX00034 | Arduino Nano 33 BLE | Amazon | $26.40
3 | 1 MIKROE-5466 | MikroE Thermoclick 28 | Mikroelektronika | $11.00
4 | 1 FPR12089 | Bottom Housing | N/A | $0.00
5 | 1 FPR12090 | Upper Housing | N/A | $0.00
6 | 1 95495K18 | Rubber Feet | McMaster-Carr | $4.13
7 | 2 5862K141 | Neodymium Magnets | McMaster-Carr | $0.77
8 | 2 2.00KXBK-ND | 2k Through-hole Resistor | Digikey | $0.10
9 | 1 497-16176-2-ND | 3.3V Linear Voltage Regulator | Digikey | $0.54
10 | 1 399-9882-2-ND | 0.33 μF Ceramic Capacitor | Digikey | $0.49
11 | 1 399-9859-2-ND | 0.1 μF Ceramic Capacitor | Digikey | $0.32
12¹ | 1 99461A916 | M2 Threadforming Screws | McMaster-Carr | $8.62
[1] Only required for the enclosure variation with screw bosses


### 6.2 Circuit Diagram

### 6.3 Plastic Part 3D Print Settings

The 3D printed housing components were fabricated on a Prusa i3MK3S FDM 3D printer with a default 0.4 mm nozzle with Hatchbox PLA and the associated filament profile. The solid models were prepared using PrusaSlicer with the settings below:


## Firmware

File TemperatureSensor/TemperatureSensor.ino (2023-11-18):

#include <Adafruit_NeoPixel.h>
#include <bluefruit.h>
#include <Wire.h>
#include "IEEE11073float.h"

BLEService BLETemperatureSensor = BLEService(0x181A);
BLECharacteristic Temperature = BLECharacteristic(0x2A6E);
BLEDis bledis;
                              
int SENSOR_ADDRESS = 0x48;
uint8_t tempData[2];
float measuredTemperature = 0.0;

void setup() {
  byte error;
  Wire.begin();
  Serial.begin(115200);

  Serial.println("BLE Temperature Sensor Module v1.01");

  // Check that Temperature Sensor is connected
  Wire.beginTransmission(SENSOR_ADDRESS);
  error = Wire.endTransmission();

  Serial.print("Attempting to Initialize with I2C Device at address 0x");
  Serial.println(SENSOR_ADDRESS, HEX);

  if (error != 0) {
    Serial.print("Error - Could not interface with I2C device at address 0x");
    Serial.println(SENSOR_ADDRESS, HEX);
    while (1);
  }
  Serial.println("Temperature Sensor Initialization successful!");
  // begin initialization
  
  Bluefruit.begin();
  Bluefruit.setName("Temperature Sensor");

  bledis.setModel("Temperature Sensor Module");
  bledis.setManufacturer("FPrin LLC");
  bledis.begin();

  setupTempSensorBLE();
  
  Bluefruit.Advertising.addService(BLETemperatureSensor);
  Bluefruit.Advertising.addName();
  Bluefruit.Advertising.restartOnDisconnect(true);
  Bluefruit.Advertising.start(0);

  Serial.println("Bluetooth® device active, waiting for connections...");
  digitalWrite(LED_BLUE, LOW);
}

void loop() {

  // if a central is connected to the peripheral:
  if (Bluefruit.connected()) {
    // update temperature value every second
    // while the central is connected:
    measuredTemperature = measureTemperature(SENSOR_ADDRESS);
    Temperature.notify(tempData,sizeof(tempData));
    printTemperature();
  }
  delay(1000);
}

float measureTemperature(int address) {
  float Temperature;
  Wire.requestFrom(address, 2);
  byte buff[2];
  Wire.readBytes(buff, 2);
  //Serial.print(buff[0],DEC);
  //Serial.print("  ");
  //Serial.println(buff[1],DEC);
  if (bitRead(buff[0], 7) == 1) { // If the first bit is a 1
    Temperature = (~((buff[0] << 8) + buff[1]) + 1) * -0.0078125; // Compute Negative Temperature
  } else { // If the first bit is a 0
    Temperature = ((buff[0] << 8) + buff[1]) * 0.0078125; // Compute Positive Temperature
  }
  tempData[0] = buff[0];
  tempData[1] = buff[1];
  return Temperature;
}

void printTemperature() {
  Serial.println(measuredTemperature, 2);
}

void readConfigRegister(int address) {
  Serial.println("Press any key to fetch config byte");
  while (!Serial.available()) {}
  Serial.read();
  Serial.println("Configuration bytes: ");

  Wire.beginTransmission(address);
  Wire.write(B00000001);
  Wire.endTransmission();

  Wire.requestFrom(address, 2);
  byte buff[2];
  Wire.readBytes(buff, 2);

  Wire.beginTransmission(address);
  Wire.write(B00000000);
  Wire.endTransmission();
  Serial.println(buff[0], BIN);
  Serial.println(buff[1], BIN);
}

void setupTempSensorBLE() {
  // Start Temperature Sensor Service
  BLETemperatureSensor.begin();

  // Setup Temperature Measurement Characteristic
  Temperature.setProperties(CHR_PROPS_NOTIFY);
  Temperature.setPermission(SECMODE_OPEN, SECMODE_NO_ACCESS);
  Temperature.setFixedLen(2);
  Temperature.begin();
  Temperature.write(tempData,sizeof(tempData));
}

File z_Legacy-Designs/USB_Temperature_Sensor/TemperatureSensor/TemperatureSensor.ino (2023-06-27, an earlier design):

#include <Wire.h>

#define SENSOR_ADDRESS 72
#define LED_R 22
#define LED_G 23
#define LED_B 24

#define DEBUGG 0

float Temperature, TemperatureFiltered;
unsigned long currentTime, startTime, sampleTime;

void setup() {
  // put your setup code here, to run once:
  byte error;
  Wire.begin();
  Wire.setClock(400000UL); // initialize at 400 kHz
  Serial.begin(115200);
  
  pinMode(LED_R, OUTPUT);
  pinMode(LED_G, OUTPUT);
  pinMode(LED_B, OUTPUT);
  digitalWrite(LED_R, HIGH);
  digitalWrite(LED_B, HIGH);
  digitalWrite(LED_G, HIGH);
  while(!Serial) {}

  Serial.println("Temperature Sensor Module v1.03");
  digitalWrite(LED_G, LOW);
  
  Wire.beginTransmission(SENSOR_ADDRESS);
  error = Wire.endTransmission();

  Serial.print("Attempting to Initialize with I2C Device at address 0x");
  Serial.println(SENSOR_ADDRESS,HEX);

  if (error != 0) {
    Serial.print("Error - Could not interface with I2C device at address 0x");
    Serial.println(SENSOR_ADDRESS,HEX);
    while(1);
  }
  Serial.println("Temperature Sensor Initialization successful!");

  if(DEBUGG) {
    readConfigRegister(SENSOR_ADDRESS);
  }
  
  Serial.println("Enter Sampling interval in seconds:");
  while(!Serial.available()) {}
  sampleTime = Serial.parseInt();
  sampleTime = constrain(sampleTime,1,86400);
  Serial.print("Sample Time set for ");
  Serial.print(sampleTime);
  Serial.println(" seconds");
  digitalWrite(LED_G, HIGH);
  
  startTime = millis();
  Temperature = measureTemperature(SENSOR_ADDRESS);
  TemperatureFiltered = Temperature;
  sampleTime = sampleTime * 1000; // Convert to ms
}

void loop() {
  // put your main code here, to run repeatedly:
  currentTime = millis();
  Temperature = measureTemperature(SENSOR_ADDRESS);
  updateFilteredTemperature(0.05);
  if((currentTime - startTime) >= sampleTime) {
    printTemperature();
    startTime = currentTime;
  }
  delay(250);
}

float measureTemperature(byte address) {
  float Temperature;
  Wire.requestFrom(address, 2);
  byte buff[2];
  Wire.readBytes(buff, 2);
  //Serial.print(buff[0],BIN);
  //Serial.print("  ");
  //Serial.println(buff[1],BIN);
  if (bitRead(buff[0],7) == 1) { // If the first bit is a 1
    Temperature = (~((buff[0] << 8) + buff[1]) + 1) * -0.0078125; // Compute Negative Temperature
  } else { // If the first bit is a 0
    Temperature = ((buff[0] << 8) + buff[1]) * 0.0078125; // Compute Positive Temperature
  }
  return Temperature;
}

void printTemperature() {
  digitalWrite(LED_B, LOW);
  Serial.println(Temperature,2);
  digitalWrite(LED_B, HIGH);
}

void updateFilteredTemperature(float alpha) {
  alpha = constrain(alpha, 0.0, 1.0);
  float previousTemperatureFiltered = TemperatureFiltered;
  TemperatureFiltered = previousTemperatureFiltered + alpha*(Temperature - previousTemperatureFiltered);
}

void readConfigRegister(byte address) {
  Serial.println("Press any key to fetch config byte");
  while(!Serial.available()) {}
  Serial.read();
  Serial.println("Configuration bytes: ");
  
  Wire.beginTransmission(address);
  Wire.write(B00000001);
  Wire.endTransmission();

  Wire.requestFrom(address,2);
  byte buff[2];
  Wire.readBytes(buff,2);

  Wire.beginTransmission(address);
  Wire.write(B00000000);
  Wire.endTransmission();
  Serial.println(buff[0],BIN);
  Serial.println(buff[1],BIN);
}

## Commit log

2023-06-27 Temperature Sensor Rev 1.0 Uploaded
    Uploaded:
    - CAD for both configurations
    - CAD for SW native
    - Arduino Sketch for control
    - User Manual
    - .3MF files for 3D Printed Components
    [FPR05-00_1_BOM_Temperature Sensor Module.xlsx, Housing-ScrewBoss.3mf, Housing-SnapFit.3mf]
2023-07-12 Initial Creation of Matlab App and ESP32 FW
    - Basic Matlab UI app implemented with:
    -- Connection to BLE devices
    -- Real-time plotting of temperature data
    -- Logging temperature data to CSV file
    - ESP32 FW:
    -- Added environmental monitoring service for temperature data
2023-08-25 Changed delay structure between updates to BLE char
    [TestData20230712_1.csv, TestData20230713_1.csv, TestData20230717_1.csv, TestData_1.xlsx]
2023-09-14 Temperature Sensor Rev 1 Design Files Update
    - Updated CAD files to most recent version
    - Updated user manual to reflect CAD
    - Updated 3D printing STL and STEP files
    [FPR05-00_1_BOM_Temperature Sensor Module.xlsx, FPR12089-03-ScrewBoss.STEP, FPR12089-03-ScrewBoss.STL, FPR12089-03-SnapFit.STEP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]
2023-09-15 Added images of Sensor Module
2023-10-28 Updated to work with nRF52840
    Updated to work with Adafruit nRF52840 feather dev board. Now uses Bluefruit BLE library
2023-11-03 Cleaned up Folder Structure
    - Changed folder structure
    - Removed unused files
    [2011 2000mAh Battery.step, 5862K141.SLDPRT, 95495K18.SLDPRT, 99461A916.SLDPRT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]
2023-11-10 Update TemperatureSensorDataLogger.mlapp
    - Fixed time axis limit error
    - Added warning for CSV write when the CSV is open
    - Added detection for disconnected BLE
    - Switched plot x axis to 24 hr format
2023-11-10 Update FPR12104-00_1_RPT_Wireless Temperature Sensor Module User Manual.pdf
    - Added note to close CSV files for datalogging
2023-11-29 Re-named Directories to remove spaces
    [FPR05-00_1_BOM_Temperature Sensor Module.xlsx, FPR12096-00_1_BOM_Temperature_Sensor_Module.xlsx, FPR12097.STEP, FPR12097.STL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]
2023-12-04 Updated folder names to not include spaces
    [FPR05-00_1_BOM_Temperature Sensor Module.xlsx, Housing-ScrewBoss.3mf, Housing-SnapFit.3mf]
